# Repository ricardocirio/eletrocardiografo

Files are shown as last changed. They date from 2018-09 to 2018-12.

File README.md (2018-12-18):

# Eletrocardiógrafo

Projeto para a disciplina PIN22107 do curso de Graduação em Engenharia Eletrônica do Instituto Federal de Santa Catarina. Consiste na concepção e execução de um eletrocardiógrafo de baixo consumo energético capaz de adquirir um sinal de eletrocardiograma por meio de 3 eletrodos e enviar suas medições para um aplicativo de aparelho celular.

## Especificações de projeto
* Energizado por bateria, portanto apresentando baixo consumo energético.

* Capaz de medir sinais entre 0,05 e 100 Hz, permitindo visualização e análise da morfologia do sinal cardíaco humano com propriedade.

## Etapas do projeto
* **Aquisição do sinal:** Por meio de eletrodos conectados ao paciente, verificando e garantindo a proteção do mesmo, com processo de isolamento do sistema. Os sinais obtidos diretamente dos eletrodos tem amplitude reduzida, atingindo 1 mV com uma frequência na faixa entre 0,05 e 100 Hz. Desse modo, para uma melhor visualização e manipulação, uma etapa de amplificação é necessária, tomando cuidado com a rejeição de ruído de modo comum.

* **Filtros:** Um filtro passa faixa deve ser implementado para seleção da banda de operação desejada, podendo ser composto por um passa altas em série com um passa baixas e, além disso, deve-se atentar para o fato de que a frequência da rede elétrica pode interferir no sinal e, portanto, deve ser removida por meio de um filtro rejeita faixa, com alto fator de qualidade.

* **Adequação do sinal:** Além de um ajuste de offset, é necessário implementar um controle de ganho que adeque a amplitude do sinal, preparando-o para digitalização por meio de um ADC.

* **Digitalização:**  A conversão do sinal analógico para digital pode ser realizada através de um conversor dedicado ou até mesmo por meio do conversor integrado de algum microcontrolador, como por exemplo o ATMEGA328p.

* **Processamento digital:** Envio dos dados via Bluetooth para o aplicativo de celular.

## Fluxograma
Para uma melhor organização e visualização das etapas necessárias, foi construído o seguinte fluxograma:
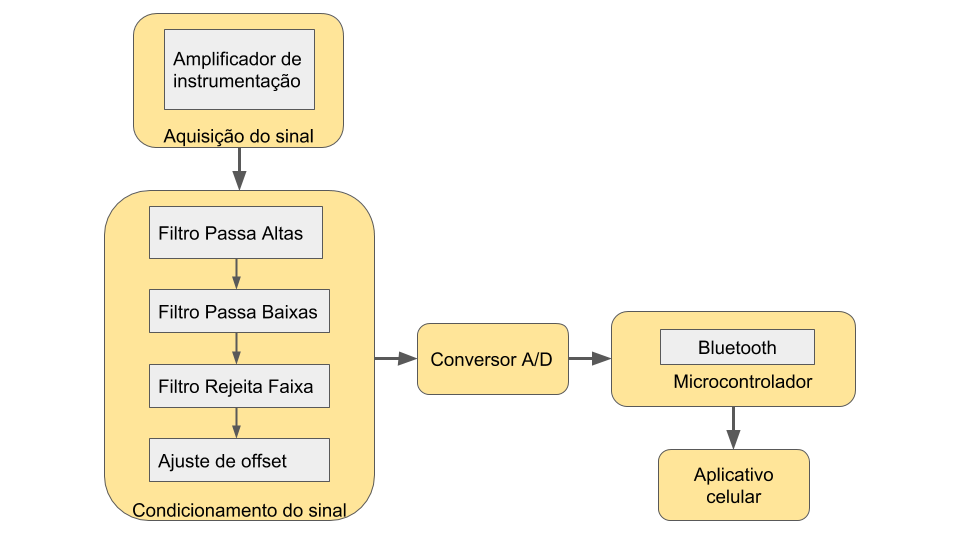
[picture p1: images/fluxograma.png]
Fluxograma


## Aquisição do sinal
Contando com um amplificador de instrumentação de alta relação sinal-ruído (SNR), o estágio inicial de amplificação faz a leitura do sinal diferencial entre os eletrodos esquerdo e direito, ao mesmo tempo que injeta uma referência por meio de um terceiro eletrodo conectado ao paciente.

O esquemático do circuito utilizado nesse estágio pode ser verificado a seguir, sendo baseado no circuito proposto e verificado na folha de dados do próprio fabricante:

<p align="center">
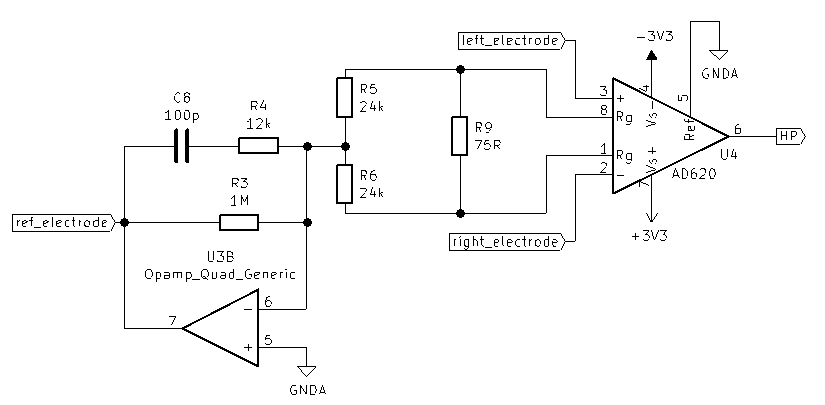
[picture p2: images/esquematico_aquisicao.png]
Esquemático AD620

</p>

## Filtros
Os filtros passa-baixas, passa-altas e rejeita-faixa foram projetados conforme o equacionamento descrito pelo livro "Amplificadores Operacionais e Filtros Ativos". As simulações foram realizadas no _software_ LTspice XVII. Foi definido inicialmente ganho unitário para todos os filtros.

### Passa-altas
Projetou-se o filtro passa-altas com ganho unitário na estrutura _voltage-controlled voltage source_ (VCVS).

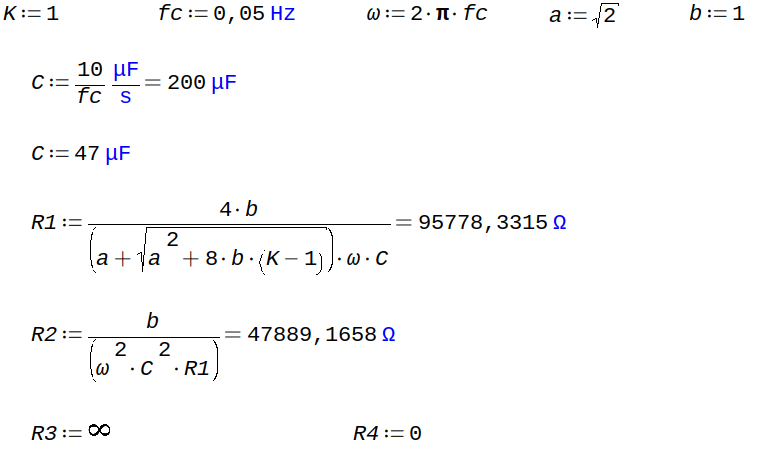
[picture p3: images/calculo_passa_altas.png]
Cálculo do filtro passa-altas


Por meio do uso do software de simulação, o comportamento resultante do filtro é:

<p align="center">
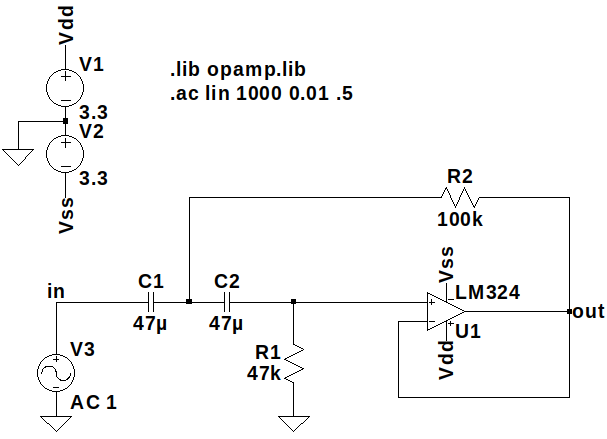
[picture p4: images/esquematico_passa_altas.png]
Esquemático do filtro passa-altas


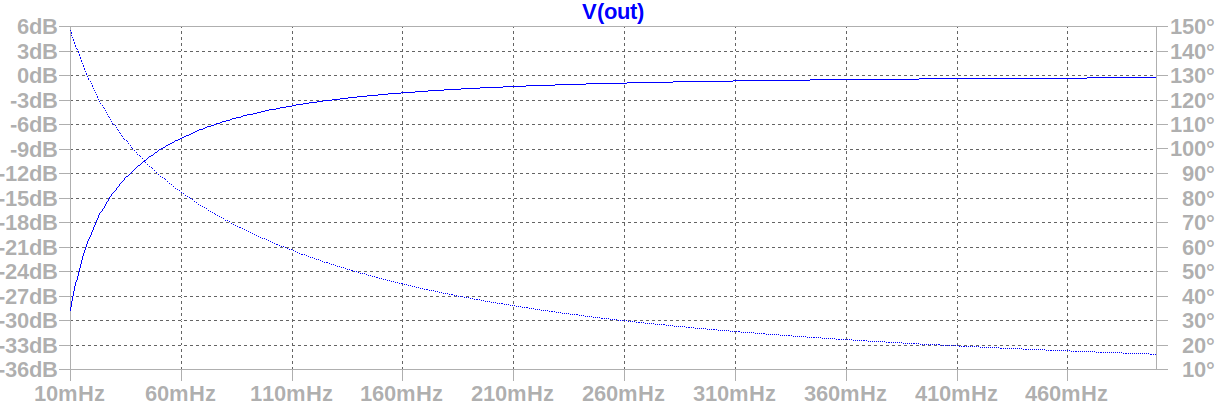
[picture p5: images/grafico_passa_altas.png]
Gráfico de simulação do filtro passa-altas

</p>

### Passa-baixas
Abaixo é possível seguir a sequência de passos utilizados na construção do filtro passa-baixas:

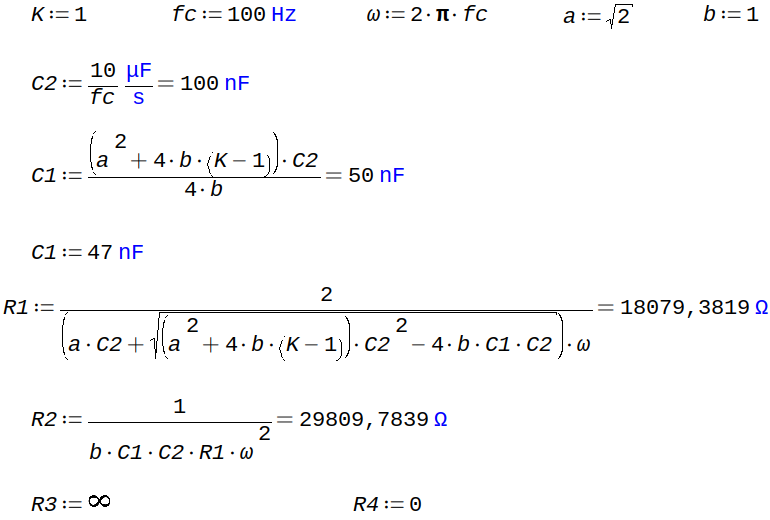
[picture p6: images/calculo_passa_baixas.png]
Cálculo do filtro passa-baixas


No intuito de otimizar a eficiência energética do eletrocardiógrafo, foi analisada a possibilidade de implementar um filtro passa-baixas passivo, portanto foi realizada uma comparação entre o filtro projetado de 2ª ordem com um filtro passivo na simulação.

<p align="center">
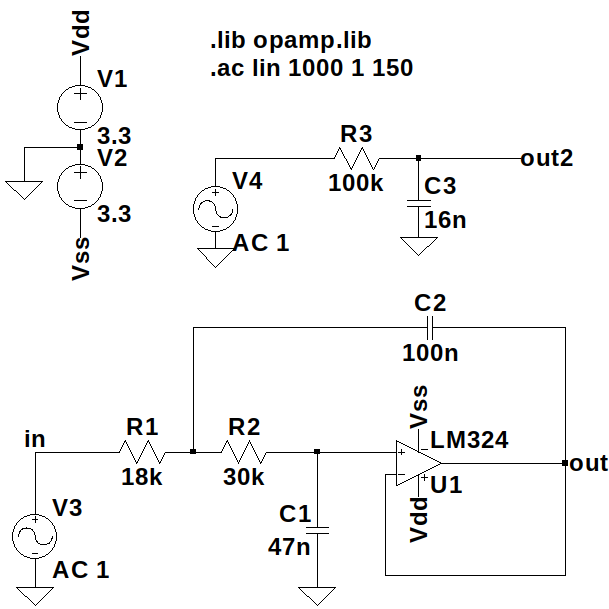
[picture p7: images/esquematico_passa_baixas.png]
Esquemático do filtro passa-baixas


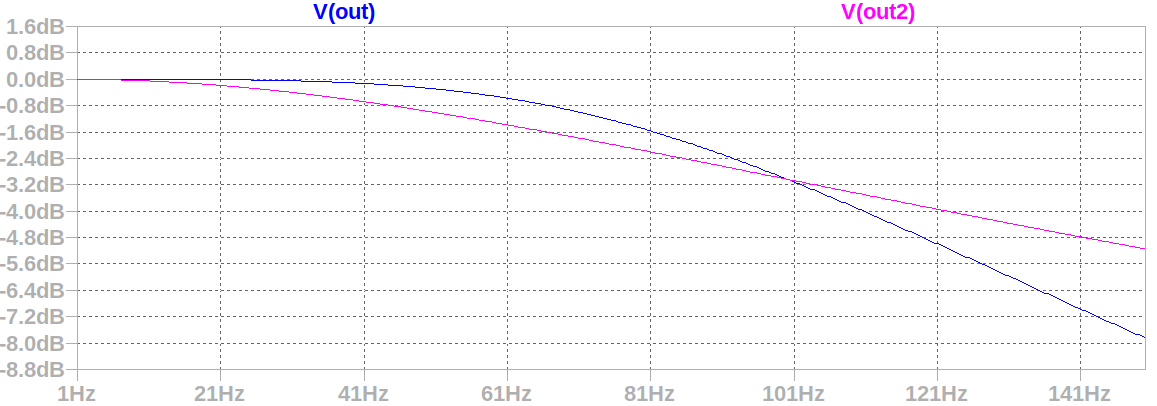
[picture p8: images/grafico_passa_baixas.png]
Gráfico de simulação do filtro passa-baixas

</p>

Apesar da economia de componentes apresentada pelo filtro passivo, sua atenuação na banda passante é indesejada e, portanto, optou-se pela utilização do filtro de 2ª ordem, que apresenta ainda decaimento de 40 dB por década na rejeição e consequentemente um fator de qualidade mais elevado.

### Rejeita-faixa

Inicialmente, projetou-se o filtro notch ativo para rejeitar ruídos oriundos da rede elétrica de 60 Hz.

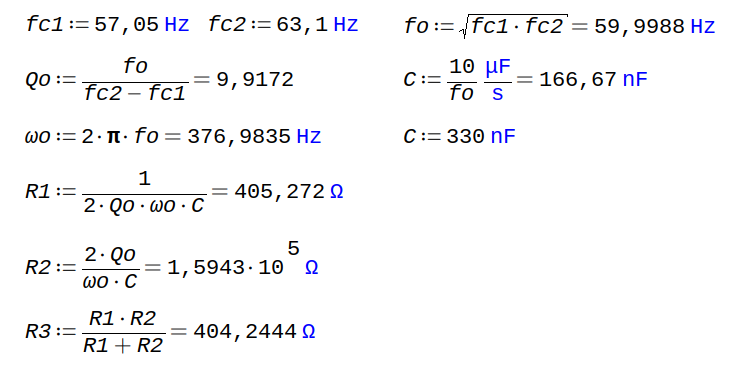
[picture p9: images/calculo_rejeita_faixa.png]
Cálculo do rejeita-faixa


<p align="center">
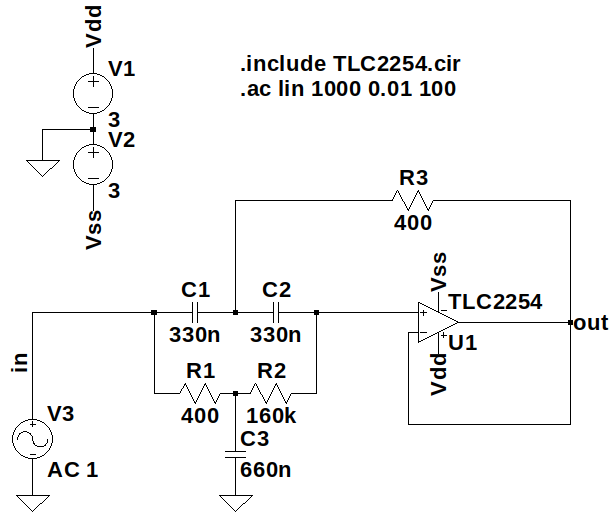
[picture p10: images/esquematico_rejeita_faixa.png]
Esquemático do filtro rejeita-faixa


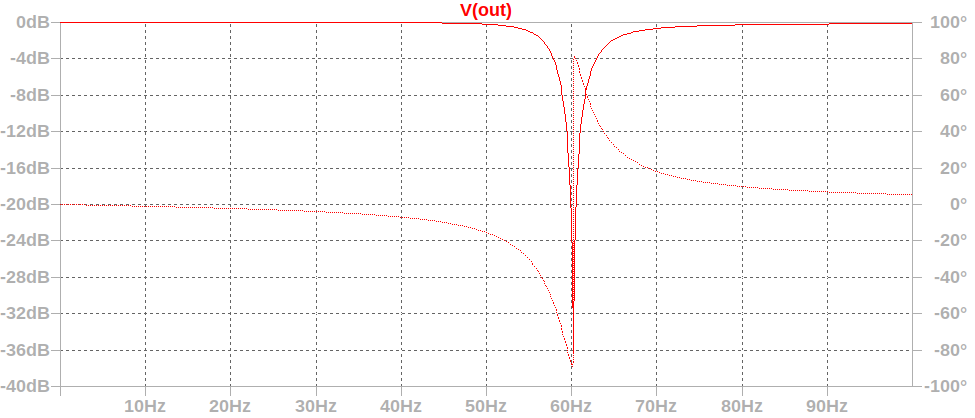
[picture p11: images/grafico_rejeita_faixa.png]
Gráfico de simulação do filtro rejeita-faixa

</p>

Entretanto, devido à sensibilidade deste filtro aos valores dos componentes utilizados, e a necessidade de um elevado fator de qualidade, concluiu-se que implementá-lo digitalmente seria uma alternativa mais apropriada. Além disso, pelo fato do circuito ser alimentado via bateria, a interferência da rede é fortemente reduzida, embora não completamente eliminada.

## Automatic Gain Control (AGC)

Ao longo do projeto, verificou-se que seria interessante a implementação de um ajuste de ganho automático devido à incerteza na amplitude do sinal de entrada, já que o mesmo varia conforme o biotipo do paciente e disposição dos eletrodos, possibilitando que a amplificação seja insuficiente ou demasiada.

Após analisar e estudar diversas maneiras de implementar um sistema de adequação do sinal, buscando obter uma excursão adequada e constante para diferentes amplitudes de entrada, surgiu como uma solução conveniente a ideia de um controle de ganho automático (AGC) por meio de um amplificador operacional não-inversor com a resistência de um JFET participando de sua realimentação negativa e influenciando diretamente em seu ganho de amplificação.

Embora seja possível controlar a resistência do JFET apropriadamente através da aplicação de um PWM gerado pelo microcontrolador que adquire o sinal, isso exige mais processamento do mesmo e consequentemente eleva seu consumo energético. Sendo assim, a alternativa escolhida foi a de controlar esse sistema de maneira analógica.

Com o auxílio do LTSpice, traçou-se, em simulação, a curva da resistência Rds em função da tensão Vgs do BF245B, transistor selecionado para o circuito.

<p align="center">
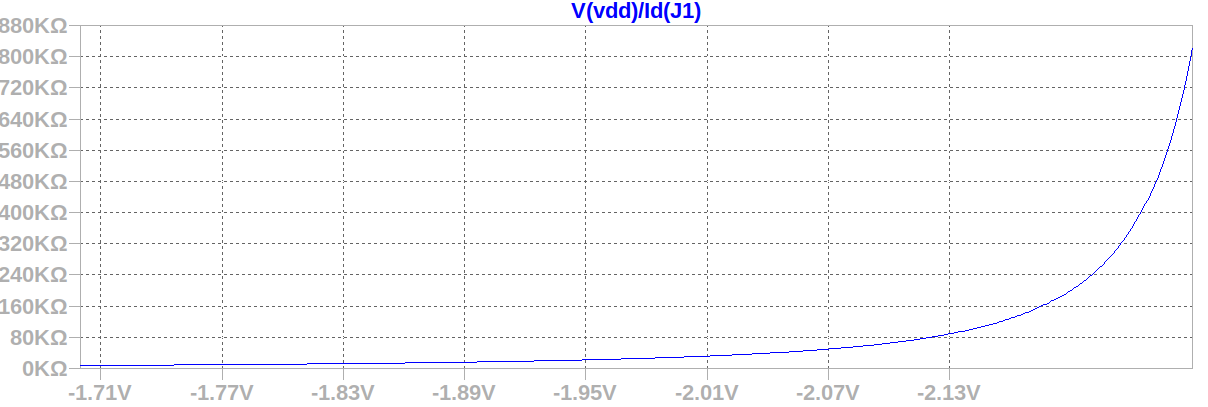
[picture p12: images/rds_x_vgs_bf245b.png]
Rds x Vgs (BF245B)

</p>

É notável a grande variação em sua resistência que ocorre em um pequeno intervalo de variação de Vgs. Devido a isso, percebe-se que é por volta desse intervalo que o JFET deve operar. Logo, projetou-se um circuito para fechar a malha de realimentação do AGC, constituído de um retificador de precisão inversor com ajuste de ganho, que detecta e inverte a tensão de pico positiva do sinal, mantendo o valor negativo obtido, utilizado para controlar o estrangulamento no canal do transistor, controlando sua condutividade. 

<p align="center">
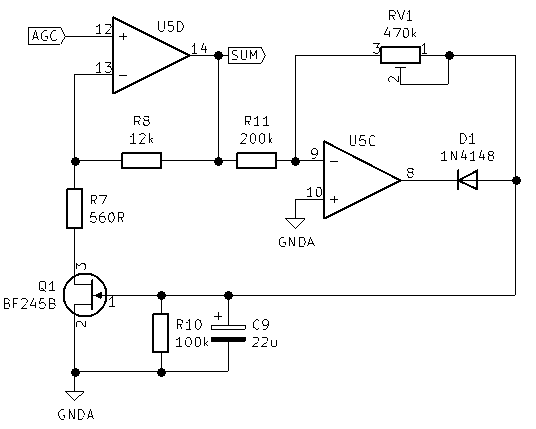
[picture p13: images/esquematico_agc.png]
Esquemático do AGC

</p>

O ajuste de ganho da realimentação, proporcionado pelo trimpot RV1, permite que se encontre o ponto ideal de operação do BF245B e também possibilita a definição de um valor limite para o sinal amplificado pelo AGC.

## Somador

Na intenção de adequar o sinal de saída para uma conversão AD fez com que surgisse a necessidade de inserir um deslocamento de nível no sinal de saída, o deixando completamente positivo. A maneira mais eficiente encontrada faz o uso de um circuito somador não-inversor, visto na figura a seguir:

<p align="center">
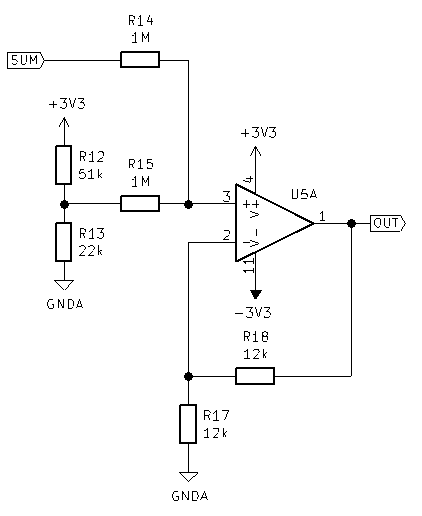
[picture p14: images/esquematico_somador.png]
Esquemático do somador

</p>

Mesmo que várias fontes tratem o circuito inversor como mais indicado e até mesmo mais difundido, a escolha pela utilização de um somador não-inversor procurou manter a ideia de um estágio genérico entre os outros, sem levar em conta se o sinal que entrava nele era invertido ou não, já que a presença de um sinal invertido na saída pode ser corrigida com a simples inversão dos conectores dos eletrodos.

Outra parte importante no projeto do somador se deu pela adição de dois resistores de alto valor (1 Megaohm), de maneira a proporcionar um casamento entre as impedâncias de saída do AGC (a própria impedância de saída do amplificador utilizado) e a de entrada do somador (entrada do amplificador empregado).

## Hardware

* **Protótipo inicial**

Em um primeiro momento, para validar os circuitos projetados até aquele momento, optou-se pela confecção de um protótipo contendo apenas os estágios de aquisição e filtragem do sinal. Já na intenção de condicioná-lo para uma conversão AD, por meio de um microcontrolador, existiu a necessidade de um ajuste de _offset_, tornando o sinal de saída completamente positivo. 

<p align="center">
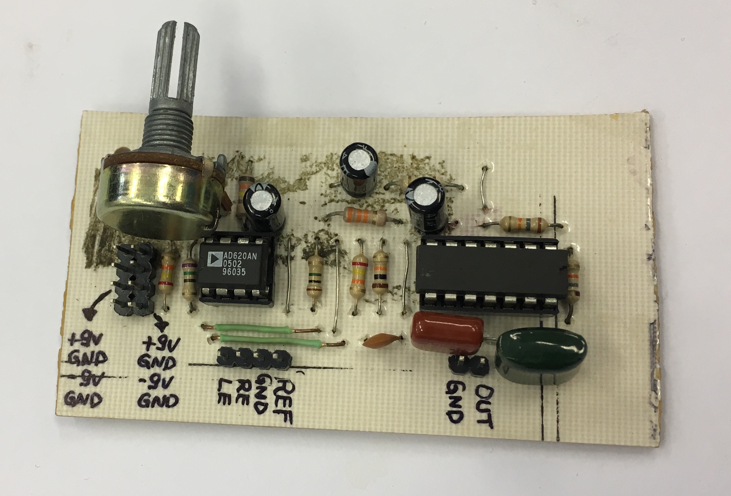
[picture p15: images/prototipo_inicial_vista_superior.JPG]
Prototipo inicial desenvolvido

</p>

A alternativa aparentemente mais prática e econômica foi a de inserir esse acréscimo no valor de tensão já no próprio filtro passa-altas, considerando que a topologia de um filtro ativo MFB (_Multiple Feedback_) permite um deslocamento do nível de tensão apenas injetando a tensão desejada na entrada não-inversora do amplificador operacional envolvido no circuito. Ao contrário do esperado, o _offset_ não se comportou corretamente, pois mesmo com ganho unitário nos filtros seguintes, o sinal de saída apresentou grande instabilidade.

<p align="center">
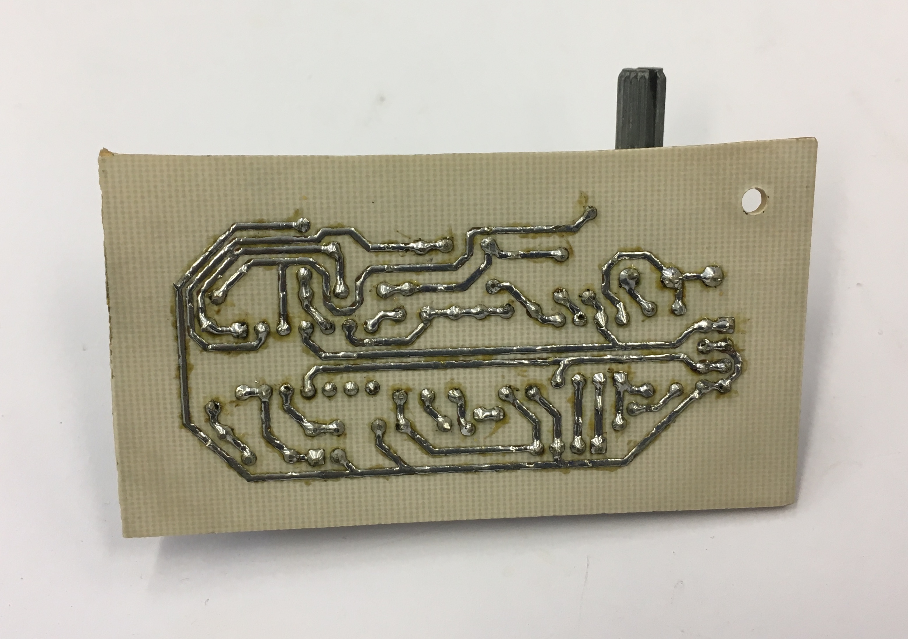
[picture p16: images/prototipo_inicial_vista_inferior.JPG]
Prototipo inicial desenvolvido

</p>

Além disso, o ajuste de ganho do sistema foi inserido por meio de um potenciômetro em série com o resistor de ganho do AD620. Observou-se, entretanto, que essa topologia deixa a desejar pelos valores de ganho muito elevados para esse estágio, já que nele o sinal ainda não foi filtrado e portanto componentes em frequências indesejadas também são amplificadas.

Para ilustrar, a seguir, é possível ver o esquemático que descreve o circuito utilizado no protótipo inicial:

<p align="center">
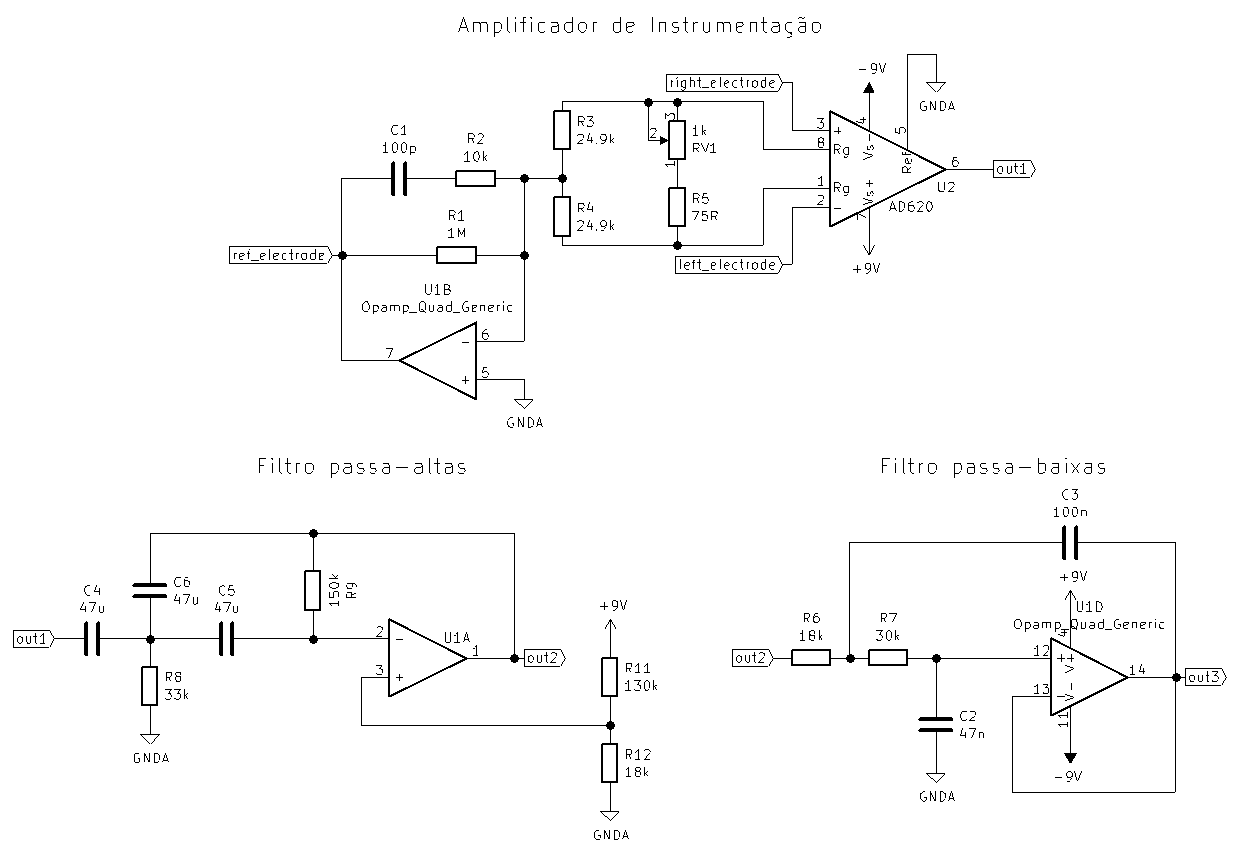
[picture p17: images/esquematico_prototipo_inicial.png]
Esquemático do protótipo inicial desenvolvido

</p>

Percebe-se que o circuito é energizado por uma alimentação simétrica de 9V, proveniente de duas baterias. Ainda, abaixo é possível ver o layout da placa de circuito impresso resultante:

<p align="center">
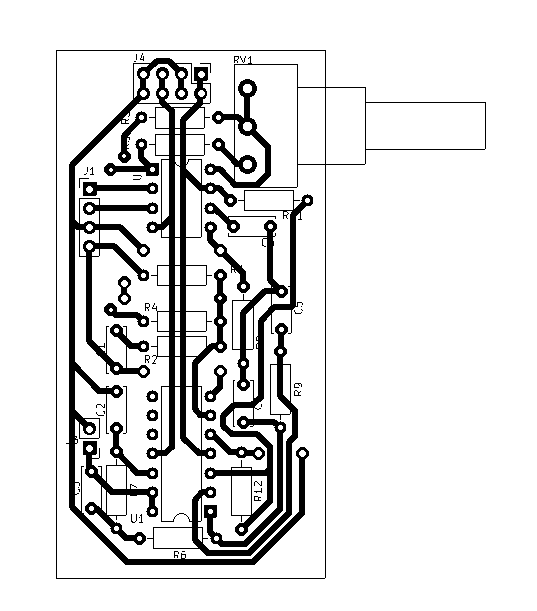
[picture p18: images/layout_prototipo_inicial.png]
Layout de placa do protótipo inicial

</p>

* **Placa final**

Levando em conta os problemas encontrados no protótipo inicial, a solução adotada com relação ao _offset_ foi de aplicá-lo em um estágio próprio, consistindo de um somador não-inversor, só no final do circuito, evitando que esse deslocamento de nível de tensão atrapalhasse o funcionamento das etapas anteriores, como os filtros e o próprio AGC.

<p align="center">
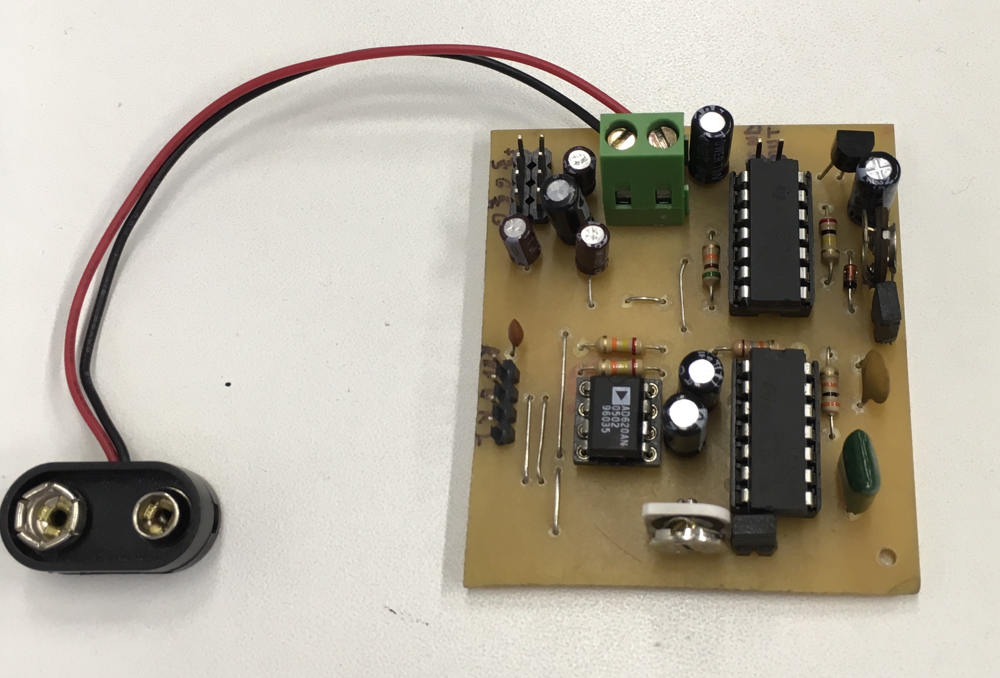
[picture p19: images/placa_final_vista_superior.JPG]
Placa final confeccionada

</p>

Pensando no consumo energético e estabilidade do sistema, foi estabelecido que todos os circuitos seriam energizados com alimentação simétrica regulada de 3.3V. Por conseguinte, foi introduzida uma regulação da tensão de alimentação positiva utilizando o regulador linear _low-dropout_ LM1117. Em sequência, visando praticidade, projetou-se a obtenção da tensão de alimentação negativa através do inversor TPS60401. Isso flexibilizou o sistema com relação a sua tensão de entrada, podendo ser energizado por uma única bateria de valor de tensão entre 4.75 e 10V.

Outro ponto importante na construção e adequação do funcionamento da nova placa desenvolvida, consistiu na seleção dos ganhos envolvidos em cada etapa de maneira a manter um valor final de amplificação equilibrado que não trouxesse instabilidade ao conjunto. Um exemplo disso foi o ganho definido para o estágio do amplificador de instrumentação.

Por apresentar uma característica de amplificação com alta relação sinal-ruído (SNR), pareceu interessante o estabelecimento do maior ganho possível nesse estágio, de maneira a eliminar ao máximo o ruído do sinal adquirido. A seleção do ganho do circuito de aquisição é diretamente dependente do valor de resistência selecionado para o resistor R9, entre os pinos 1 e 8 do AD620 (estágio de aquisição). Na intenção de deixar o sistema independente de um ajuste manual, antes regulado pelo potenciômetro adicionado, a ideia passou a ser de fixar o valor desse resistor, inicialmente 75 ohms, resultando em um ganho próximo a 660. 

Com esse ganho estabelecido, a aquisição do sinal se deu de maneira eficiente, apresentando uma boa amplitude para o sinal de saída e uma satisfatória atenuação do ruído envolvido. Com a adição dos filtros, o sinal de saída alcançou as características desejadas para o circuito.

<p align="center">
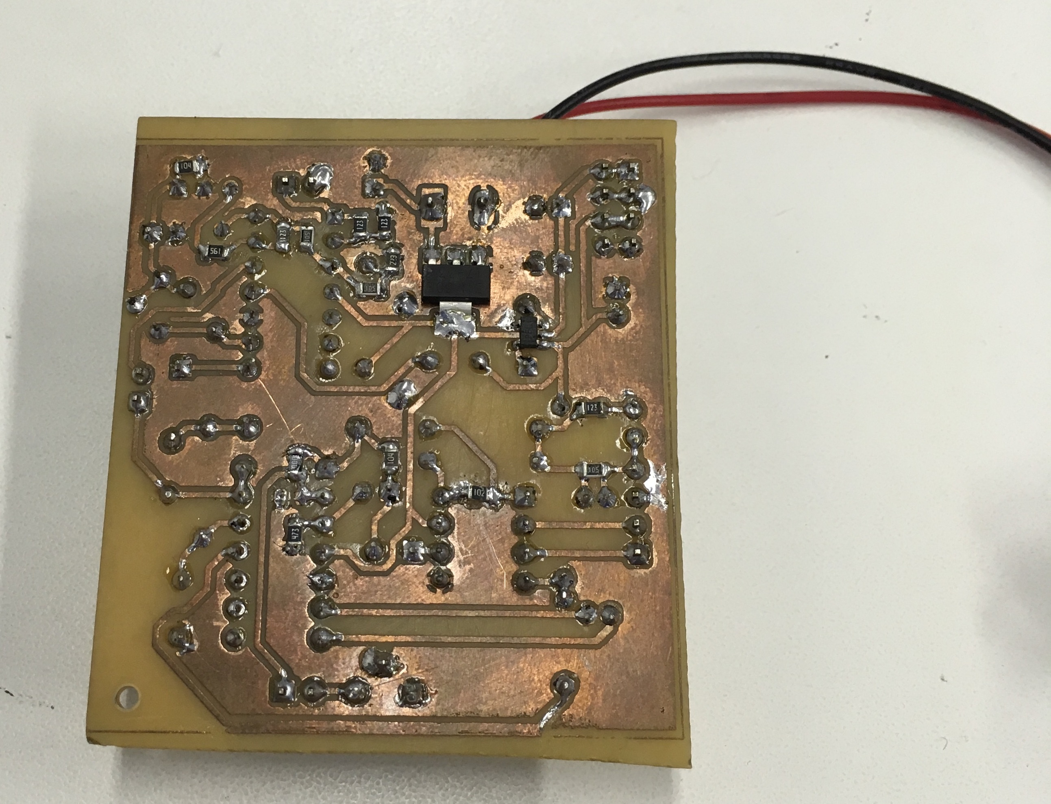
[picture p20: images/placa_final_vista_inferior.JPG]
Placa final confeccionada

</p>

A partir da decisão de adicionar o estágio de controle de ganho, este proporcionou certas limitações em relação ao sinal condicionado pelos primeiros estágios: com um funcionamento adequado do AGC apenas para sinais de entrada com valores de tensão entre 50 e 500 mVpp, o ganho definido para o estágio de aquisição se tornou absurdo, já que o sinal fornecido ao estágio de controle automático de ganho já se encontrava fora dos limites determinados, deixando o sinal de saída instável e oscilando entre as saturações negativa e positiva do amplificador operacional, demonstrando um valor exagerado de amplificação.

Desse modo, ajustes foram feitos e um novo resistor tomou o lugar do R9, com valor igual a 1 kohms, resultando em um ganho próximo a 50 e permitindo que o ganho excedente necessário fosse proporcionado pelo próprio AGC. Com estes ajustes, os problemas de saturação foram corrigidos e o pleno funcionamento do estágio do AGC foi alcançado.
Funcionando como esperado, o somador não-inversor adicionado ao final cumpriu plenamente seu papel, resultando em uma saída do eletrocardiógrafo limitada a um valor de aproximadamente 1 Vpp e um _offset_ também de 1 VCC, adequado à janela estabelecida de 3.3 V limitados pela alimentação do sistema, que também acaba ditando o valor máximo de tensão para o ADC.

Por fim, o resultado foi uma placa de circuito impresso, empregando dessa vez alguns componentes do tipo SMD disponíveis para o projeto, de maneira a distribuí-los melhor e diminuir o tamanho físico de placa necessário para a construção do projeto.

<p align="center">
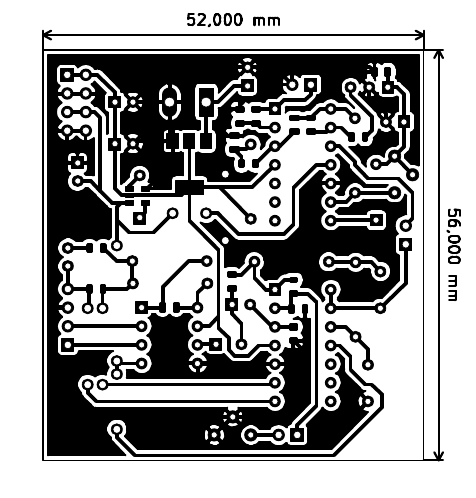
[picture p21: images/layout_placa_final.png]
Layout da placa final

</p>

## Software

Depois de todo o processo de construção do eletrocardiógrafo, dispositivo preocupado em evidenciar o formato do sinal emitido pela pulsação cardiovascular, é importante encontrar uma maneira de mostrar graficamente a saída do conjunto. Para esta tarefa, a escolha de uma conexão por meio de um transmissor Bluetooth visou a praticidade de uma conexão sem fio e também por ser uma ferramenta democrática, já que todos os smartphones atuais contam com esse tipo de conexão, o que leva à criação de um produto de mais fácil utilização e adaptação.

O transmissor Bluetooth escolhido para a tarefa é um módulo do tipo HC-05, que utiliza a comunicação UART do microcontrolador para receber e enviar informações do mesmo. Para a visualização gráfica, foi utilizado um aplicativo para smartphones com sistema operacional Android, gratuito, e facilmente encontrado na loja de aplicativos. Nesse aplicativo, o envio de uma _string_ contendo o valor lido no ADC em um formato reconhecido pelo software permitiu que a onda fosse visualizada de maneira bem prática.  

## Resultados

Depois de toda a etapa de projeto, é importante a validação dos resultados esperados, verificando se os objetivos do projeto foram alcançados. 

Na figura a seguir, é possível verificar o sinal de saída do eletrocardiógrafo, obtido com o auxílio de um osciloscópio:

<p align="center">
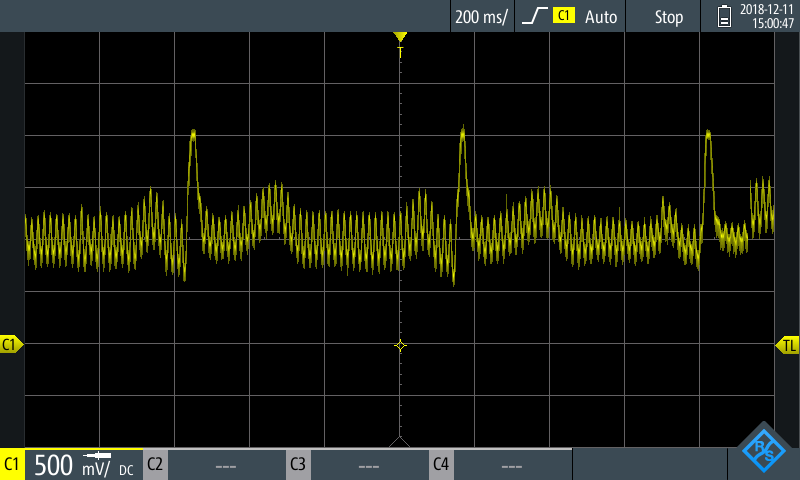
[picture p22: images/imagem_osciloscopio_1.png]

</p>

O sinal visto na imagem acima traz algumas informações importantes sobre as validações do projeto: primeiramente, é possível ver um sinal de mais alta frequência sobreposto ao do ECG, este que é a influência eletromagnética causada pela própria rede de distribuição, com sua frequência de 60 Hz, e que acaba afetando o circuito que é eletromagneticamente sensível. Além disso, frequências muito mais altas podem ser verificadas sobre o sinal, na ordem dos MHz, provenientes de ondas de radiofrequência que transitam pelo ambiente e que não conseguem ser filtradas.

A presença da frequência de 60 Hz na saída do circuito era esperada, já que esta se encontra na faixa de operação do sistema (0.05 - 100 Hz), e deveria ser eliminada pelo filtro rejeita-faixa idealizado anteriormente mas que, por sua alta precisão de projeto, se tornou inviável. Parte dessa interferência já é diminuída por conta do uso de baterias para a alimentação do circuito, isolando o circuito de ruídos conduzidos, entretanto, não o blindando de possíveis ruídos irradiados. Na parte da medição, o uso de um osciloscópio desligado da rede, também alimentado por baterias, permitiu a visualização do sinal também com menor interferência.

No caso das componentes de mais alta frequência, idealmente, essas deveriam ser eliminadas pelo filtro passa-baixas implementado, evitando essa interferência. O que acontece, é que na prática o amplificador operacional utilizado nos filtros não é capaz de trabalhar em frequências muito altas, como as presentes no sinal. O modelo que usamos para a implementação (LM324) tem um bom funcionamento para frequências até a ordem de algumas centenas de kHz, no máximo poucos MHz, o que o deixa impossibilitado de eliminar as frequências indesejadas. Por questão de esclarecimento, foi testado isoladamente o filtro passa-baixas e verificado que sua frequência de corte se encontra nos 100 Hz esperados e que os ruídos decorrem mesmo da não-idealidade do amplificador operacional. 

Com a praticidade do osciloscópio, independente da rede de energia, foi possível desligar os outros equipamentos ligados nos arredores da montagem, verificando o nível de interferência de sua emissão de ondas eletromagnéticas. Ainda, o uso de um limitador de banda do osciloscópio, com o intuito de facilitar a visualização, eliminando as frequências que o próprio circuito era incapaz de lidar, resultou na imagem a seguir:

<p align="center">
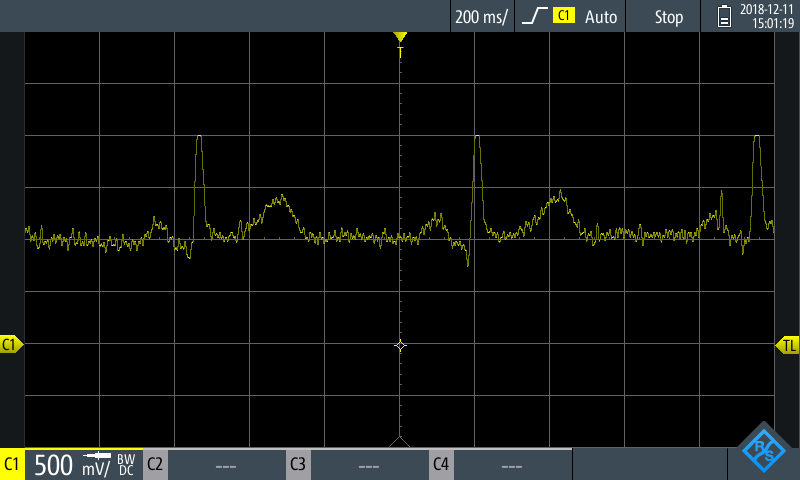
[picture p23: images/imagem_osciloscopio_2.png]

</p>

Em relação ao sinal visualizado por meio do aplicativo, empregando uma conexão Bluetooth, pode ser vista a seguir uma captura da tela do smartphone utilizado:

<p align="center">
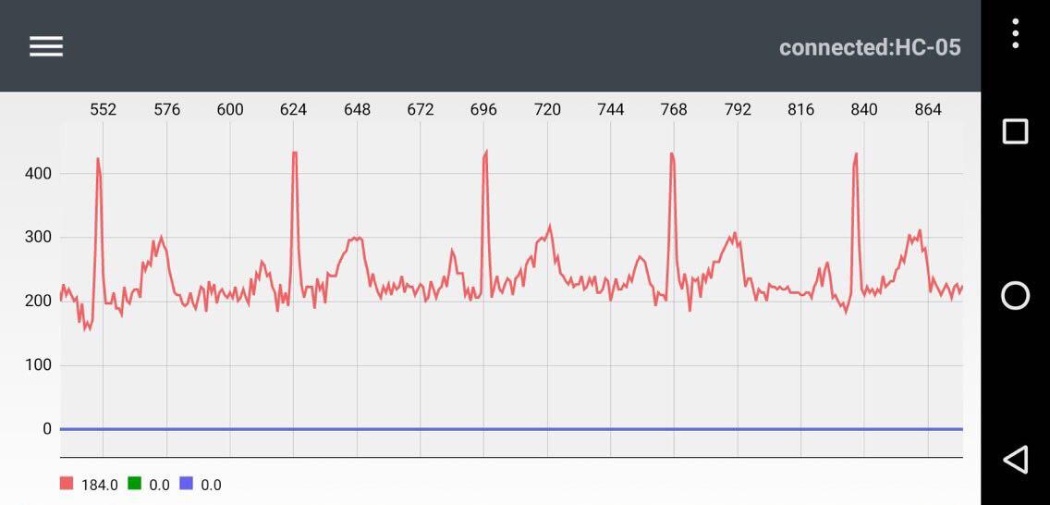
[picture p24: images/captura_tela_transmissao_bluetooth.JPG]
Imagem do aplicativo com o sinal recebido via conexão Bluetooth

</p>

O sinal verificado no aplicativo não apresenta as componentes de frequência da ordem dos MHz, isso por conta da própria taxa de amostragem do sinal e da transmissão do Bluetooth, que acabam por “alisar” a curva.

## Consumo energético

O consumo da placa final de aquisição e condicionamento do sinal é estimado em aproximadamente 135.9mW. Esse valor representa o “pior caso”, pois foi obtido considerando: o consumo máximo de 1,2mA em cada canal dos LM324, incluindo os dois não utilizados; a corrente máxima de 1,3mA do AD620; a potência dissipada no regulador LM1119, considerando a bateria de 9V utilizada nos testes; e a eficiência de cerca de 97,5% do inversor TPS60401, apresentada quando o mesmo opera em 3,3V suprimindo as correntes de alimentação mencionadas para os amplificadores operacionais e de instrumentação.

Analisando à parte a potência dissipada pela parte digital do sistema, verifica-se que o microcontrolador ATmega328p consome cerca de 16,5mW operando ativamente em 16MHz e alimentado com +3,3V. Já o módulo bluetooth apresenta consumo médio de 82,5mW.

Considerando uma bateria de 9V comum, fornecendo uma quantidade de energia próxima a 500mAh, seria possível alimentar o circuito responsável pela aquisição e condicionamento do sinal (sem a transmissão bluetooth) por até 33 horas ininterruptas, com esse tempo podendo aumentar significativamente ao usar baterias com maior capacidade. Se o microcontrolador e módulo bluetooth forem considerados, o funcionamento ininterrupto sob as condições mencionadas chega a 19 horas.

## Sugestões para trabalhos futuros

* Naturalmente, algumas melhorias podem ser feitas a fim de se conseguir melhores resultados com o circuito implementado: para diminuir a interferência do sinal oscilatório de 60 Hz, proveniente da rede, seria possível a implementação de um filtro rejeita-faixa digital, utilizando o próprio microcontrolador que nesse momento faz apenas o trabalho da transmissão Bluetooth;

* Como maneira de blindar o circuito contra as interferências eletromagnéticas, a construção do circuito envolvido por um gabinete metálico traria melhores resultados, minimizando tanto a interferência da rede elétrica quanto as altas frequências que conseguem passar pelos filtros.

* O consumo energético pode ser minimizado ainda mais com a utilização de baterias de tensão próxima à mínima suportada, redução da frequência de operação do microcontrolador, bem como desabilitação de seus periféricos não utilizados e possivelmente utilização do modo _sleep_ entre leituras do ADC e envio de dados via bluetooth.

## Autores
* João Vitor Bassani
* Ricardo Schons Cirio

## Bibliografia
1. PERTENCE Jr., A. **Amplificadores Operacionais e Filtros Ativos**. 7.ed. Porto Alegre: Artmed, 2012.

2. SEDRA, A. S; SMITH, K. C. **Microeletrônica**. 5 ed. São Paulo: Pearson / Prentice Hall, 2010.

3. BOYLESTAD, R. e NASHELSKY, L. **Dispositivos eletrônicos e teoria de circuitos**. 8 ed. Prentice Hall do Brasil. Rio de Janeiro. 2005.

4. Analog Devices. **AD620**. Disponível em: <https://www.analog.com/media/en/technical-documentation/data-sheets/AD620.pdf>. Acesso em 16/12/2018.

5. On Semiconductor. **LM324**. Disponível em: <https://www.onsemi.com/pub/Collateral/LM324-D.PDF>. Acesso em 16/12/2018.

6. Texas Instruments. **LM1117**. Disponível em: <http://www.ti.com/lit/ds/symlink/lm1117.pdf>. Acesso em 16/12/2018.

7. Texas Instruments. **TPS6040x**. Disponível em: <http://www.ti.com/lit/ds/symlink/tps60400.pdf>. Acesso em 16/12/2018.

8. Atmel. **ATmega328P**. Disponível em: <http://ww1.microchip.com/downloads/en/DeviceDoc/Atmel-7810-Automotive-Microcontrollers-ATmega328P_Datasheet.pdf>. Acesso em 16/12/2018.

9. Makezine. **HC Serial Bluetooth Products**. Disponível em: <https://cdn.makezine.com/uploads/2014/03/hc_hc-05-user-instructions-bluetooth.pdf>. Acesso em 16/12/2018.

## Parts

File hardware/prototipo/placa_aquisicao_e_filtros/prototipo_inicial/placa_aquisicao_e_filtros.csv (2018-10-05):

Id | Designator | Package | Quantity | Designation | Supplier and ref
1 | R13,R13,R13,R13,R13,R13,R13,R13 | R_Axial_DIN0207_L6.3mm_D2.5mm_P10.16mm_Horizontal | 8 | 0
2 | R11,R11,R11,R11,R11,R11,R11,R11 | R_Axial_DIN0207_L6.3mm_D2.5mm_P10.16mm_Horizontal | 8 | 130k
3 | C2,C2,C2,C2,C2,C2,C2,C2 | C_Disc_D6.0mm_W2.5mm_P5.00mm | 8 | 47n
4 | U2,U2,U2,U2,U2,U2,U2,U2 | DIP-8_W7.62mm | 8 | AD620
5 | R4,R3,R4,R3,R4,R3,R4,R3,R4,R3,R4,R3,R4,R3,R3,R4 | R_Axial_DIN0207_L6.3mm_D2.5mm_P10.16mm_Horizontal | 16 | 24.9k
6 | RV1,RV1,RV1,RV1,RV1,RV1,RV1,RV1 | Potentiometer_Piher_PC-16_Single_Horizontal | 8 | 1k
7 | R12,R12,R12,R12,R12,R12,R12,R12 | R_Axial_DIN0207_L6.3mm_D2.5mm_P10.16mm_Horizontal | 8 | 18k
8 | J3,J3,J3,J3,J3,J3,J3,J3 | PinHeader_1x02_P2.54mm_Vertical | 8 | Conn_01x02
9 | R8,R8,R8,R8,R8,R8,R8,R8 | R_Axial_DIN0207_L6.3mm_D2.5mm_P10.16mm_Horizontal | 8 | 91k
10 | R9,R9,R9,R9,R9,R9,R9,R9 | R_Axial_DIN0207_L6.3mm_D2.5mm_P10.16mm_Horizontal | 8 | 47k
11 | J4,J4,J4,J4,J4,J4,J4,J4 | PinHeader_2x04_P2.54mm_Vertical | 8 | Conn_02x04_Counter_Clockwise
12 | C5,C4,C5,C4,C5,C4,C5,C4,C5,C4,C5,C4,C5,C4,C4,C5 | C_Disc_D6.0mm_W2.5mm_P5.00mm | 16 | 47u
13 | U1,U1,U1,U1,U1,U1,U1,U1 | DIP-14_W7.62mm | 8 | Opamp_Quad_Generic
14 | R1,R1,R1,R1,R1,R1,R1,R1 | R_Axial_DIN0207_L6.3mm_D2.5mm_P10.16mm_Horizontal | 8 | 1M
15 | R2,R2,R2,R2,R2,R2,R2,R2 | R_Axial_DIN0207_L6.3mm_D2.5mm_P10.16mm_Horizontal | 8 | 10k
16 | R6,R6,R6,R6,R6,R6,R6,R6 | R_Axial_DIN0207_L6.3mm_D2.5mm_P10.16mm_Horizontal | 8 | 18k
17 | C1,C1,C1,C1,C1,C1,C1,C1 | C_Disc_D6.0mm_W2.5mm_P5.00mm | 8 | 100p
18 | R10,R10,R10,R10,R10,R10,R10,R10 | R_Axial_DIN0207_L6.3mm_D2.5mm_P10.16mm_Horizontal | 8 | 0R
19 | C3,C3,C3,C3,C3,C3,C3,C3 | C_Disc_D6.0mm_W2.5mm_P5.00mm | 8 | 100n
20 | C6,C6,C6,C6,C6,C6,C6,C6 | C_Disc_D6.0mm_W2.5mm_P5.00mm | 8 | 47u
21 | J1,J1,J1,J1,J1,J1,J1,J1 | PinHeader_1x04_P2.54mm_Vertical | 8 | Conn_01x04
22 | R5,R5,R5,R5,R5,R5,R5,R5 | R_Axial_DIN0207_L6.3mm_D2.5mm_P10.16mm_Horizontal | 8 | 75R
23 | R7,R7,R7,R7,R7,R7,R7,R7 | R_Axial_DIN0207_L6.3mm_D2.5mm_P10.16mm_Horizontal | 8 | 30k

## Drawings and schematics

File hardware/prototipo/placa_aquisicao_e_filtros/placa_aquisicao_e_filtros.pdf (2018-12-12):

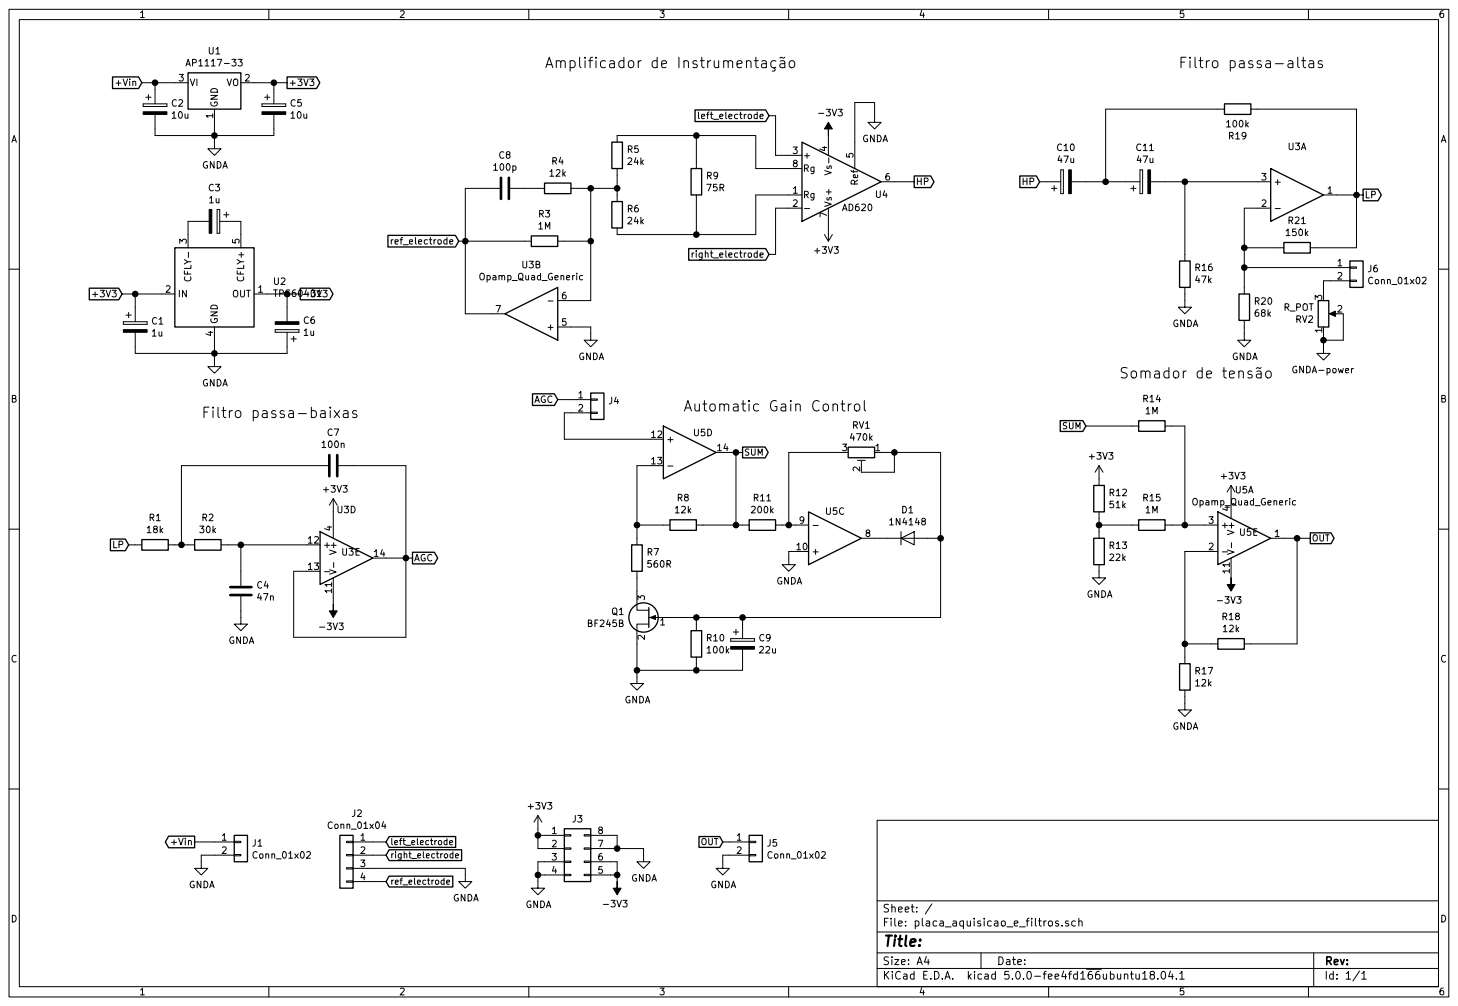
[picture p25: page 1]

22k +3V3 GNDA Somador de tensão

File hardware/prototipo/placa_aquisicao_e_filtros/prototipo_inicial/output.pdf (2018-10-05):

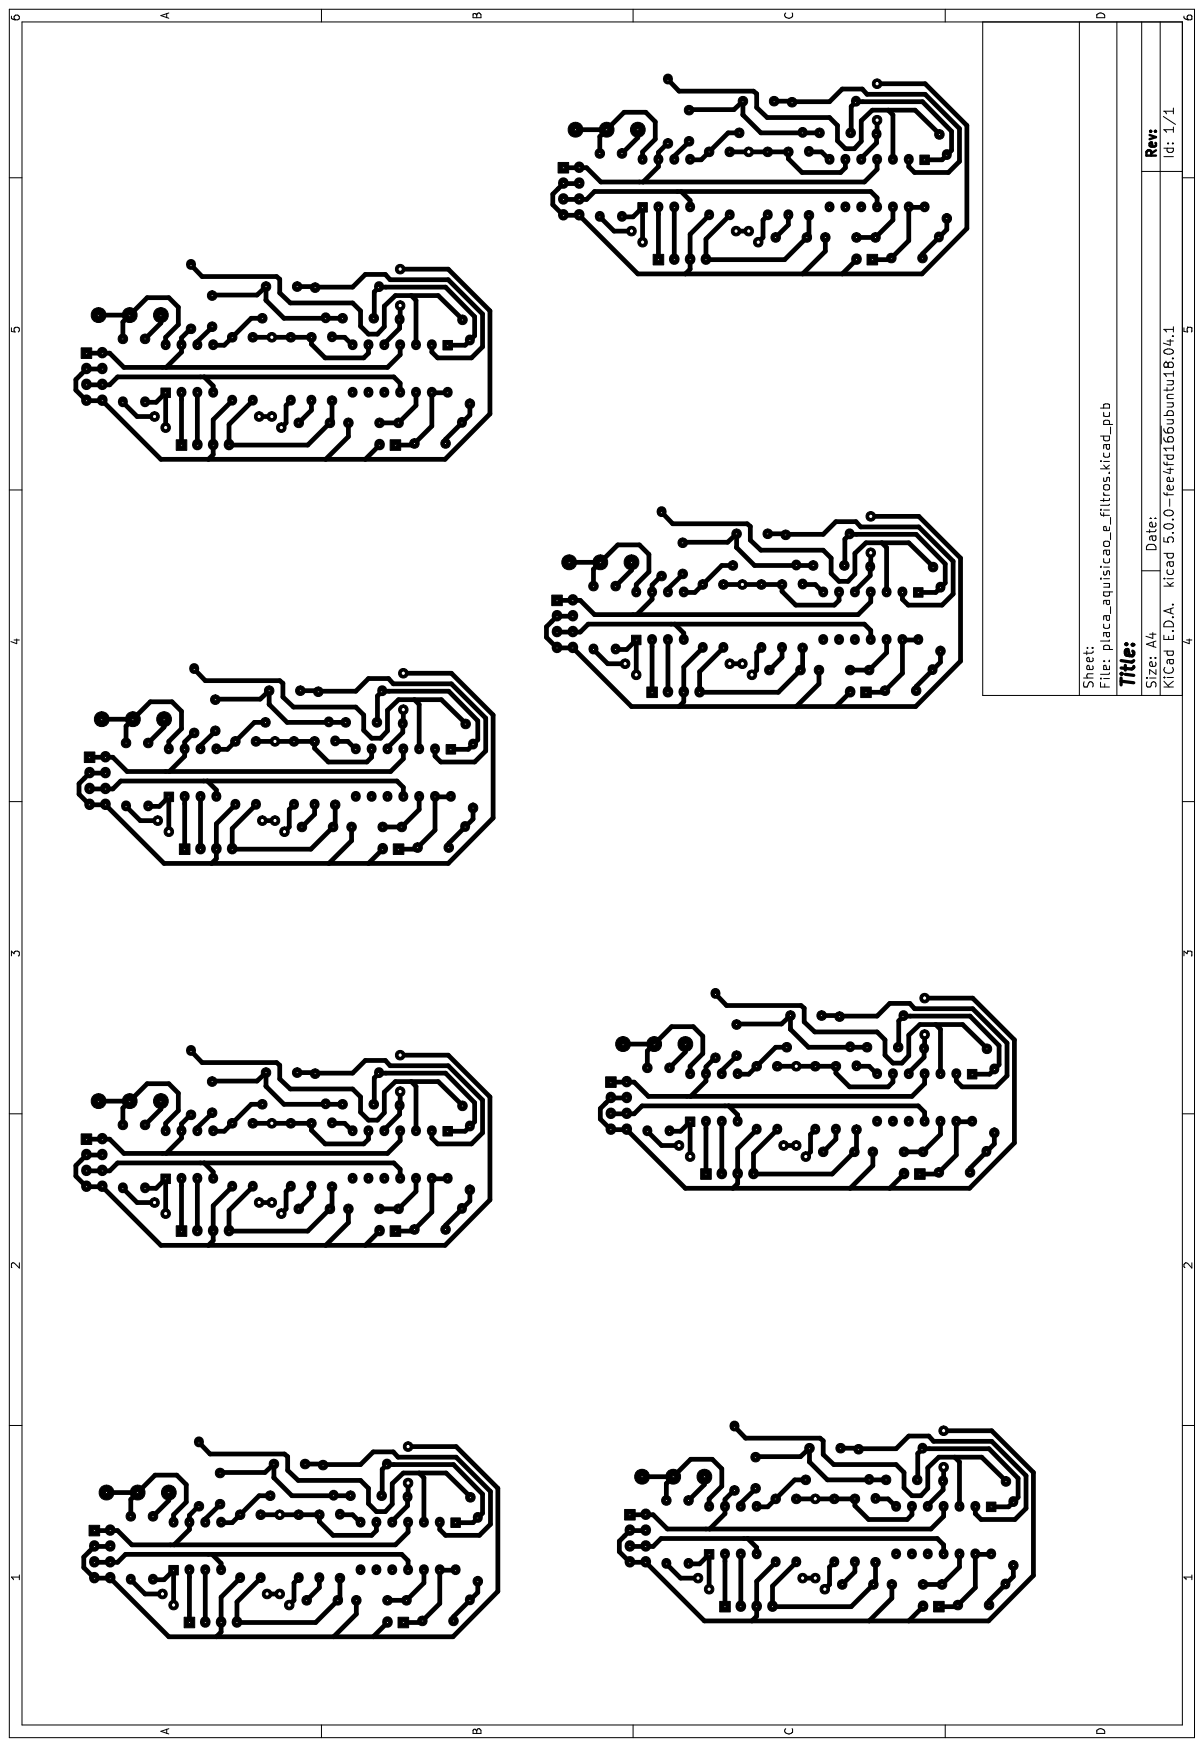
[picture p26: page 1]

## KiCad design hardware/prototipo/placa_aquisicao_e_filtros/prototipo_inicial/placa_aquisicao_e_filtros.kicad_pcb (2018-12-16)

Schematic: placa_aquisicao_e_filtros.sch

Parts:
C1: 100p; C_Disc_D6.0mm_W2.5mm_P5.00mm
C2: 47n; C_Disc_D6.0mm_W2.5mm_P5.00mm
C3: 100n; C_Disc_D6.0mm_W2.5mm_P5.00mm
C4, C5, C6: 47u; C_Disc_D6.0mm_W2.5mm_P5.00mm
J1: Conn_01x04; PinHeader_1x04_P2.54mm_Vertical
J3: Conn_01x02; PinHeader_1x02_P2.54mm_Vertical
J4: Conn_02x04_Counter_Clockwise; PinHeader_2x04_P2.54mm_Vertical
R1: 1M; R_Axial_DIN0207_L6.3mm_D2.5mm_P10.16mm_Horizontal
R2: 10k; R_Axial_DIN0207_L6.3mm_D2.5mm_P10.16mm_Horizontal
R3, R4: 24.9k; R_Axial_DIN0207_L6.3mm_D2.5mm_P10.16mm_Horizontal
R5: 75R; R_Axial_DIN0207_L6.3mm_D2.5mm_P10.16mm_Horizontal
R6, R12: 18k; R_Axial_DIN0207_L6.3mm_D2.5mm_P10.16mm_Horizontal
R7: 30k; R_Axial_DIN0207_L6.3mm_D2.5mm_P10.16mm_Horizontal
R8: 33k; R_Axial_DIN0207_L6.3mm_D2.5mm_P10.16mm_Horizontal
R9: 150k; R_Axial_DIN0207_L6.3mm_D2.5mm_P10.16mm_Horizontal
R11: 130k; R_Axial_DIN0207_L6.3mm_D2.5mm_P10.16mm_Horizontal
RV1: 1k; Potentiometer_Piher_PC-16_Single_Horizontal
U1: Opamp_Quad_Generic; DIP-14_W7.62mm
U2: AD620; DIP-8_W7.62mm

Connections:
+9V: J4.1, J4.2, R11.1, U1.4 (V+), U2.7 (Vs+)
-9V: J4.5, J4.6, U1.11 (V-), U2.4 (Vs-)
GNDA: C2.2, J1.3, J3.2, J4.3, J4.4, J4.7, J4.8, R8.1, R12.2, U1.5 (+), U2.5 (Ref)
unnamed: C1.1, R2.2
unnamed: C2.1, R7.1, U1.12 (+)
unnamed: C3.2, R6.1, R7.2
unnamed: C4.1, C5.2, C6.2, R8.2
unnamed: C5.1, R9.1, U1.2 (-)
unnamed: R1.1, R2.1, R3.2, R4.1, U1.6 (-)
unnamed: R3.1, RV1.2, RV1.3, U2.8 (Rg)
unnamed: R4.2, R5.2, U2.1 (Rg)
unnamed: R5.1, RV1.1
unnamed: R11.2, R12.1, U1.3 (+)
left_electrode: J1.1, U2.2 (-)
out1: C4.2, U2.6
out2: C6.1, R6.2, R9.2, U1.1
out3: C3.1, J3.1, U1.13 (-), U1.14
ref_electrode: C1.2, J1.4, R1.2, U1.7
right_electrode: J1.2, U2.3 (+)

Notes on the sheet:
Amplificador de Instrumentação
Filtro passa-altas
Filtro passa-baixas

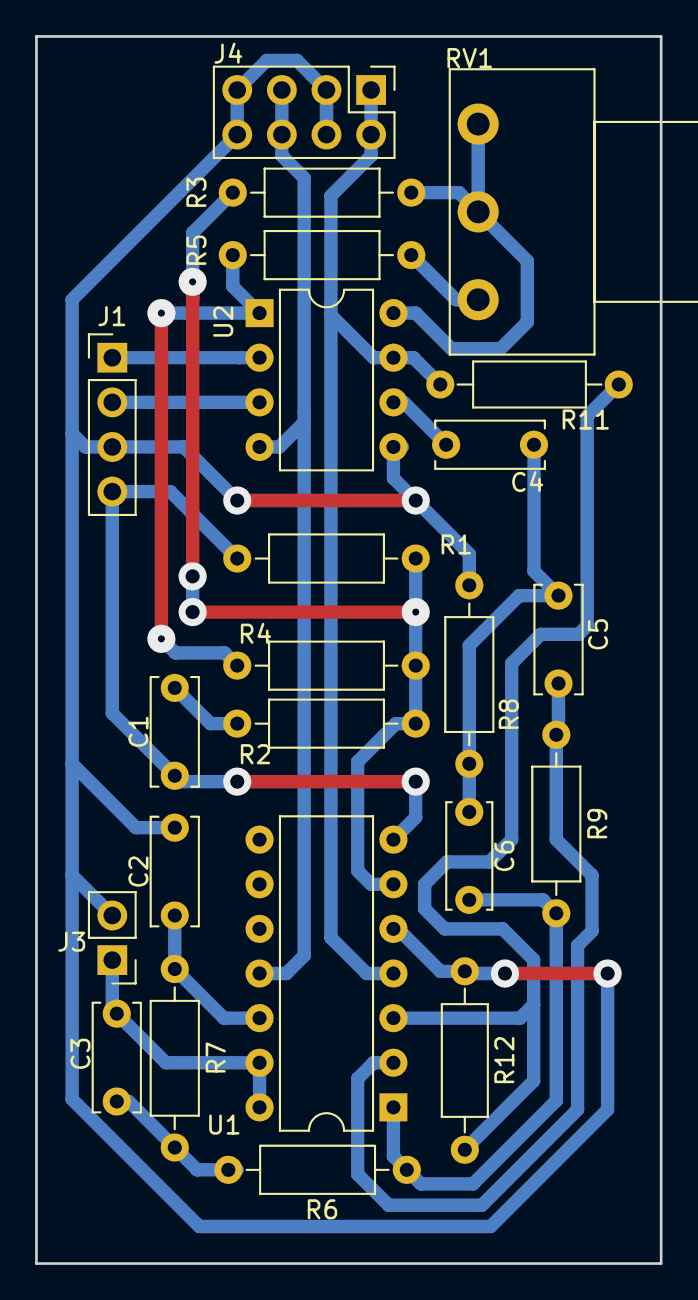
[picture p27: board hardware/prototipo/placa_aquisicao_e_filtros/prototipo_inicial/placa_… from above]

Board: 2 copper layers, 35.6 x 69.8 mm, 23 parts (0 on the bottom side), 19 nets.

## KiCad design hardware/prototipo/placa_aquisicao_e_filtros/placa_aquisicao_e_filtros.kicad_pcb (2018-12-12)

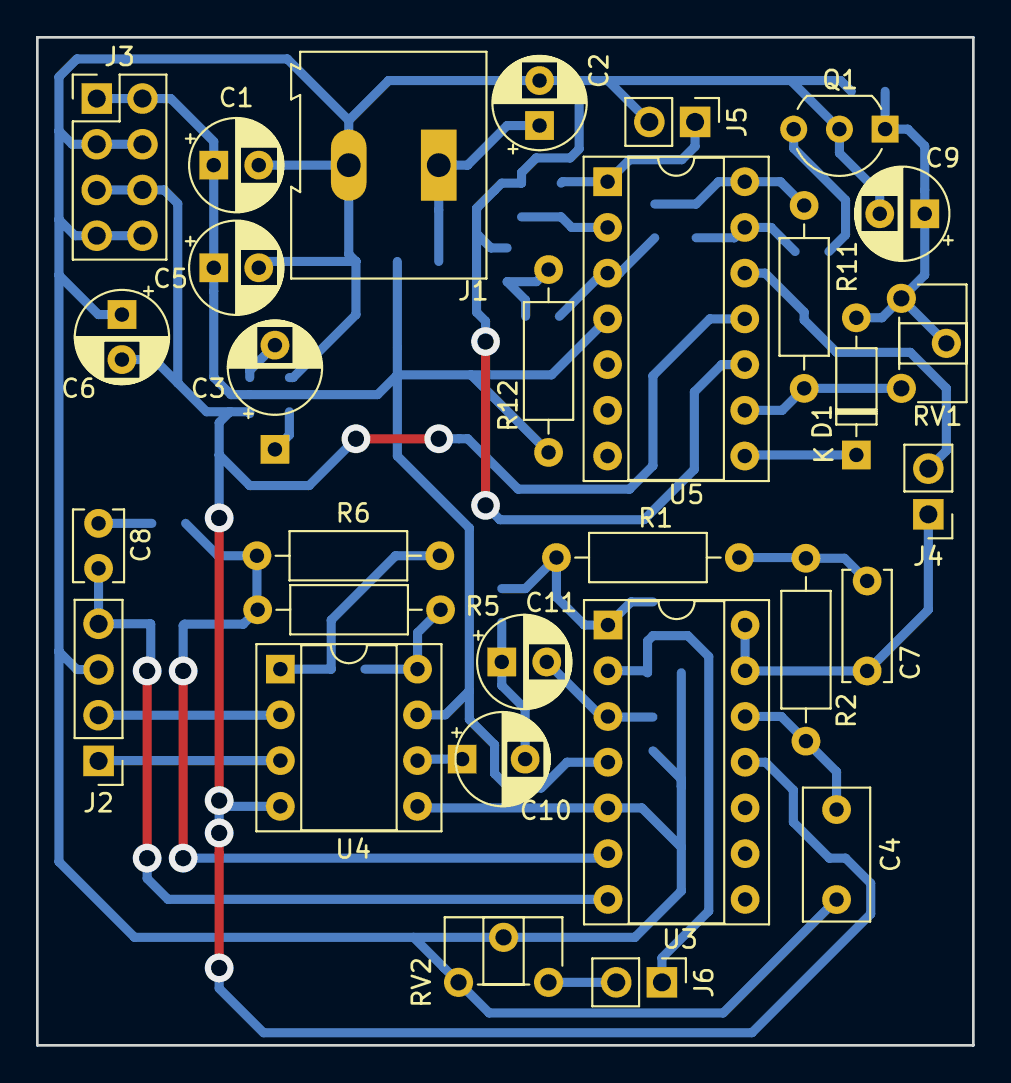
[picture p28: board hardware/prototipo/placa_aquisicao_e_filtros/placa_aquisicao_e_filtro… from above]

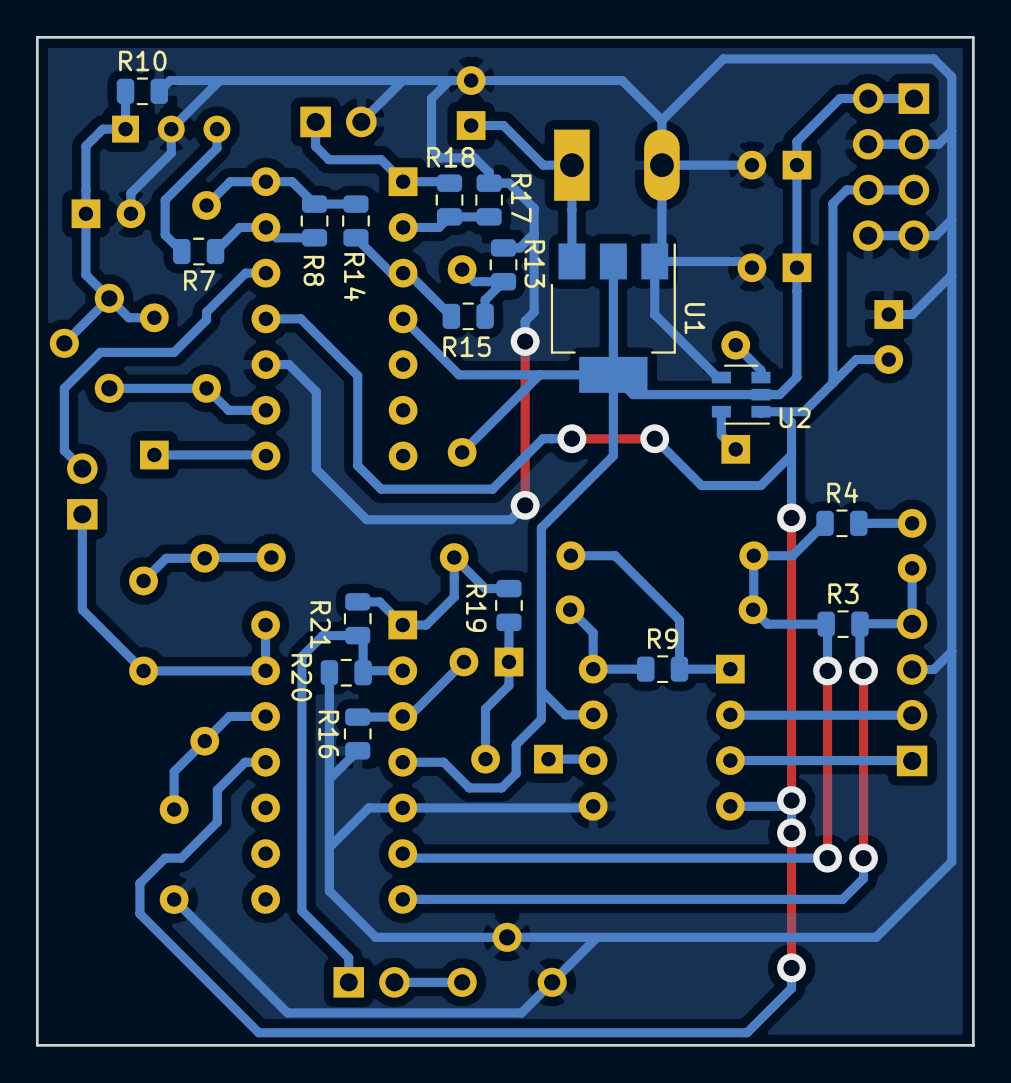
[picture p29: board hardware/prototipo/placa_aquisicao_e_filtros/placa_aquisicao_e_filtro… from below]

Board: 2 copper layers, 52.0 x 56.0 mm, 47 parts (17 on the bottom side), 33 nets.

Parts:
C1, C3, C6: 1u; CP_Radial_D5.0mm_P2.50mm
C2, C5: 10u; CP_Radial_D5.0mm_P2.50mm
C4: 47n; C_Rect_L7.2mm_W3.5mm_P5.00mm_FKS2_FKP2_MKS2_MKP2
C7: 100n; C_Disc_D6.0mm_W2.5mm_P5.00mm
C8: 100p; C_Disc_D3.8mm_W2.6mm_P2.50mm
C9: 22u; CP_Radial_D5.0mm_P2.50mm
C10, C11: 47u; CP_Radial_D5.0mm_P2.50mm
D1: 1N4148; D_DO-35_SOD27_P7.62mm_Horizontal
J1: Conn_01x02; TerminalBlock_Altech_AK300-2_P5.00mm
J2: Conn_01x04; PinHeader_1x04_P2.54mm_Vertical
J3: Conn_02x04_Counter_Clockwise; PinHeader_2x04_P2.54mm_Vertical
J4, J5, J6: Conn_01x02; PinHeader_1x02_P2.54mm_Vertical
Q1: BF245B; TO-92_Inline_Wide
R1: 18k; R_Axial_DIN0207_L6.3mm_D2.5mm_P10.16mm_Horizontal
R2: 30k; R_Axial_DIN0207_L6.3mm_D2.5mm_P10.16mm_Horizontal
R3: 1M; R_0805_2012Metric
R4, R8, R17, R18: 12k; R_0805_2012Metric
R5, R6: 24k; R_Axial_DIN0207_L6.3mm_D2.5mm_P10.16mm_Horizontal
R7: 560R; R_0805_2012Metric
R9: 75R; R_0805_2012Metric
R10, R19: 100k; R_0805_2012Metric
R11: 200k; R_Axial_DIN0207_L6.3mm_D2.5mm_P10.16mm_Horizontal
R12: 51k; R_Axial_DIN0207_L6.3mm_D2.5mm_P10.16mm_Horizontal
R13: 22k; R_0805_2012Metric
R14, R15: 1k; R_0805_2012Metric
R16: 47k; R_0805_2012Metric
R20: 68k; R_0805_2012Metric
R21: 150k; R_0805_2012Metric
RV1: 470k; Potentiometer_ACP_CA6-H2,5_Horizontal
RV2: R_POT; Potentiometer_ACP_CA6-H2,5_Horizontal
U1: AP1117-33; SOT-223-3_TabPin2
U2: TPS60401; SOT-23-5
U3, U5: Opamp_Quad_Generic; DIP-14_W7.62mm_Socket
U4: AD620; DIP-8_W7.62mm_Socket

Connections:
+3V3: C1.1, C5.1, J3.1, J3.2, R12.1, U1.2, U2.2, U3.4, U4.7, U5.4
+Vin: C2.1, J1.1, U1.3
-3V3: C6.2, J3.5, J3.6, U2.1, U3.11, U4.4, U5.11
AGC: C7.1, J4.1, U3.13, U3.14
GNDA: C1.2, C2.2, C4.2, C5.2, C6.1, C9.2, J1.2, J2.3, J3.3, J3.4, J3.7, J3.8, J5.2, Q1.2, R10.2, R13.2, R16.1, R17.2, R20.2, RV2.1, RV2.2, U1.1, U2.4, U3.5, U4.5, U5.10
HP: C10.1, U4.6
LP: R1.2, R19.2, R21.1, U3.1
unnamed: C3.1, U2.5
unnamed: C3.2, U2.3
unnamed: C4.1, R2.1, U3.12
unnamed: C7.2, R1.1, R2.2
unnamed: C8.1, R4.2
unnamed: C9.1, D1.2, Q1.1, R10.1, RV1.1, RV1.2
unnamed: C10.2, C11.1, R19.1
unnamed: C11.2, R16.2, U3.3
unnamed: D1.1, U5.8
unnamed: J4.2, U5.12
unnamed: J6.1, R20.1, R21.2, U3.2
unnamed: J6.2, RV2.3
unnamed: Q1.3, R7.2
unnamed: R3.1, R4.1, R5.2, R6.1, U3.6
unnamed: R5.1, R9.1, U4.8
unnamed: R6.2, R9.2, U4.1
unnamed: R7.1, R8.2, U5.13
unnamed: R11.1, RV1.3, U5.9
unnamed: R12.2, R13.1, R15.2
unnamed: R14.1, R15.1, U5.3
unnamed: R17.1, R18.2, U5.2
OUT: J5.1, R18.1, U5.1
SUM: R8.1, R11.2, R14.2, U5.14
left_electrode: J2.1, U4.3
ref_electrode: C8.2, J2.4, R3.2, U3.7
right_electrode: J2.2, U4.2

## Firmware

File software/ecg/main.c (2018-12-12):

/*
 * main.c
 *
 *  Created on: 24 de out de 2018
 *      Author: ricardo & joao
 */

#include <avr/interrupt.h>
#include <util/delay.h>

#include "lib/avr_usart.h"

volatile uint32_t leitura_adc;

int main()
{
	FILE *usart = get_usart_stream();

	USART_Init(B9600);

	/* Configuracao ADC
	 *
	 * ADMUX:
	 * 		-Internal 1.1V Voltage Reference with external capacitor at AREF pin
	 * 		-ADC left adjust
	 * 		-ADC0 Input
	 * ADCSRA:
	 * 		-ADC Enabled
	 * 		-ADC Start Conversion
	 * 		-Auto Trigger Enable
	 * 		-Prescaler 128
	 * ADCSRB:
	 * 		-Free running mode
	 * DIDR0:
	 * 		-ADC5...0's Digital Input Buffer Disabled
	 * */
	ADMUX = (0 << REFS1) | (1 << REFS0) | (1 << ADLAR) | (0 << 4) | (0 << MUX3) | (0 << MUX2) | (0 << MUX1) | (0 << MUX0);
	ADCSRA = (1 << ADEN) | (1 << ADSC) | (1 << ADATE) | (0 << ADIF) | (1 << ADIE) | (1 << ADPS2) | (1 << ADPS1) | (1 << ADPS0);
	ADCSRB = (0 << ADTS2) | (0 << ADTS1) | (0 << ADTS0);
	DIDR0 = (1 << ADC5D) | (1 << ADC4D) | (1 << ADC3D) | (1 << ADC2D) | (1 << ADC1D) | (1 << ADC0D);

	//_delay_ms(2000);
	//fprintf(usart, "AT+NAME=ECG_01\r\n");
	//_delay_ms(1000);

	sei();

	while (1)
	{
		leitura_adc = ((leitura_adc << 2) * 1100) / 1024;
		//fprintf(usart, "%d 0\n", leitura_adc);
		fprintf(usart, "E%d,0,0\n", leitura_adc);
		//_delay_ms(5);
	}
	return 0;
}

ISR(ADC_vect)
{
	leitura_adc = ADCH;
}

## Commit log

2018-09-06 Cronograma disponível na pasta de imagens.
2018-09-21 Filter simulations added.
2018-09-27 Acquisition PCB prototype started.
    [placa_aquisicao_e_filtros.kicad_pcb, placa_aquisicao_e_filtros.sch]
2018-09-28 Acquisition PCB prototype in development.
    [placa_aquisicao_e_filtros.kicad_pcb, placa_aquisicao_e_filtros.sch]
2018-10-05 Acquisition prototype board finalized.
    [placa_aquisicao_e_filtros.csv, placa_aquisicao_e_filtros.kicad_pcb, placa_aquisicao_e_filtros.sch]
2018-12-01 PCB with AGC routed but negative supply without voltage regulator
    [placa_aquisicao_e_filtros.csv, placa_aquisicao_e_filtros.kicad_pcb, placa_aquisicao_e_filtros.sch]
2018-12-12 Second prototype working with bluetooth.
    [placa_aquisicao_e_filtros.kicad_pcb, placa_aquisicao_e_filtros.sch]
2018-12-16 Documentation added.
    [placa_aquisicao_e_filtros.kicad_pcb, placa_aquisicao_e_filtros.sch]
